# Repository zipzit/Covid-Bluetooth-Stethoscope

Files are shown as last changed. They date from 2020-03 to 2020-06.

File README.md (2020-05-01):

# Project description:  low-cost open-source DIY wireless stethoscope designs

(from [https://helpwithcovid.com/projects/252-bluetooth-stethoscope-pulse-oximeter](https://helpwithcovid.com/projects/252-bluetooth-stethoscope-pulse-oximeter))

This is a collaborative volunteer driven project to develop designs for low-cost wireless stethoscopes that can be constructed with hobbyist-level skill and tools and provided to medical professionals using the same volunteer-driven model current being used to create and donate face shield and masks world-wide.

## The problem

High-quality stethoscopes are expensive, and stethoscopes in general are hard to sterilize.  This results in a use model where cheap stethoscopes are acquired by the hospital/clinic and one is assigned to each patient, with every professional who works with that patient using the same stethoscope.  This can result in cross-contamination as someone touches many stethoscopes.  Cheap stethoscopes also wear out quickly and have short hoses, resulting in professionals getting physically closer to the patient than necessary, particularly if they have to put their arm around the patient and listen to positions on the back.

With Covid-19 this is an even greater problem because medical professionals may be wearing full PPE and struggle to get a traditional stethoscope into their ears safely.

Like N95 masks and face shields, there is concern that stethoscopes may become a scarce commodity as the pandemic continues to spread, and poorer countries with weaker healthcare systems will particularly struggle to source in-demand equipment.

## Our goal

To create stethoscope designs that reduce the risk of infection during use and cost of manufacture, and that can be built and validated by enthusiasts or manufacturers around the world, at price points that are viable in a variety of markets.

Current digital stethoscopes on the market start at $300-$500, and can go as high as $2700/unit. We are working towards the units being effectively disposable, to the point where if a hospital *had* to assign one to each patient and then throw it away when done it wouldn’t be a financial hardship.

In designing several different models we are targeting different price points and are able to deliver the simplest design fast.

## Our solutions

In order to reduce close physical contact between patient and medical professional we need an electronic device which can amplify or transmit the internal sounds created by the heart and lungs. Our lowest-tech concept design is a single hand-held device which picks up the sounds with a microphone and amplifies it to a speaker. More advanced designs will transmit that sound via Bluetooth to an over-the-ear headset worn by the medical professional. Our goal is to have the units be easily disinfected between uses so they can be utilized on multiple patients, but cheap enough that if necessary they could be assigned to a single patient as is the case with current stethoscopes.

This project is developing rapidly and constantly evolving. We are starting the simple amplifier + speaker and Bluetooth designs in parallel with the plan that learnings from one design can be applied to others. All designs are intended to be constructed by anyone with some basic electronics knowledge and a soldering iron, and possibly access to a 3D printer.

### "Quick-and-dirty" speaker puck

The simplest concept doesn’t use a headset at all - simply a single unit with a cup/microphone, a AA-battery-powered amplifier, and a speaker. We’re currently in the prototyping stage for this using off-the-shelf electronic components that anyone should be able to order online.  If possible, we would like to use existing containers - reusing standard pill bottles for instance - to avoid having to 3D-print a housing.

Sterilization is a factor as well.  If possible, using something like a pill bottle would provide a housing that can be easily sterilized.  If not possible, units can be placed in ziploc bags that can be sterilized between patients.  

#### Current status:
We still have some basic questions to answer to prove this solution can reliably reproduce and amplify lung sounds.  We have constructed a concept unit, but decent sound quality without creating feedback is proving to be a significant roadblock.  We are testing different directional microphones, mimicing stethoscope architecture, adding insulation between microphone and speaker, and exploring a setup with two units separated by a short cable. 

### "Smarter" speaker puck

One step up from there is to replace our simple analog electronics with some digital logic and a microprocessor.  We’re looking at the ESP32, which is common and relatively cheap, and there are a number of good development platforms on the market.  It comes with integrated bluetooth and wifi (which we would use for the next model), as well as lithium-ion battery charging logic.  This would allow us to potentially do some digital signal processing of the sound, to clear up noise or amplify certain frequencies.

This will build on the knowledge we gather about microphones and speakers and housings, and will likely require some software development.  It will take longer, so is the second stage solution.

#### Current status:
We have been working with two different ESP32 development boards - the ESP32-LoRa, and the ESP32 Lyra-T Mini:

Using the Lyra-T Mini we have constructed a prototype which uses a microphone inside a standard stethscope bell and broadcasts via bluetooth to a standard bluetooth-enabled speaker.  Heart sounds appear clear and audible though a Bose Soundlink bluetooth speaker, we need more work to determine if we can reproduce decent sound quality with an onboard speaker.  The Lyra-T Mini is approximately $22/unit and has extra on-board audio codecs and ADCs.

Using the LoRa, we have tested that we can pair reliably with most standard bluetooth devices, and recover the connection if one side of the link is reset.  We have modified the Espressif-provided open-source software to do this.  The LoRa has also had issues with the I2S DMA ADC operating while bluetooth is functional.  We filed a support ticket with Espressif and they have provided a fix.  The LoRa is slightly cheaper and smaller than the Lyra-T and comes with an onboard screen.  We would like this board as a development option, but it would require adding an addition codec/ADC chip - likely the ES8388, which is approx. $1. 

### Smart bluetooth puck

One step up from there is to enable bluetooth and the ability to pair with a set of over-the-ear headphones, worn by the medical professional over their PPE gear.  This will require some case redesign to allow for a small screen and some buttons, to allow selection of the bluetooth device to pair with.  Again, it builds off what we’ve learned from the previous design, and may require more software development.

To work towards a completed design we need to:
- Integrate the stethoscope cup or accept one attached by a short tube with a microphone.
- Develop whatever DSP (Digital Signal Processing) algorithms are necessary for noise/frequency filtering or shifting.
- Find an onboard amplifier/speaker solution that can reliably reproduce lung sounds with sufficient volume. 

#### Current status:
The "Smarter" Speaker Puck and Smart Bluetooth Puck are basically the same project at this point.  Our current prototype uses a standard stethoscope cup to pick up sounds, and a bluetooth link to connect to an external speaker.

To work towards a completed design we need to:
- Integrate the stethoscope cup or accept one attached by a short tube with a microphone.
- Integrate a screen that will show available bluetooth devices to pair with. (Requires software development)
- Test connections and audio quality with different bluetooth headsets (the cheaper the better).

### Unit testing collateral

Ultimately people who are constructing units will want standard metrics to test their units against.  We have audio recordings of lung sounds that we can devleop into an audio test library.  Another open-source medical devices organization (glia.org) has developed some promising-looking testing procedures using water balloons to mimic a human body.

For initial devices we will simply try to get devices in the hands of trained medical professionals for testing, but ultimately want to develop a standardized test plan.

### However...

Having said all of this, we are not inherently attached to these solutions.  We continue to look at alternate solutions (such as repurposing cheap earpods) to see if we can create better, cheaper, or more "quick-and-dirty" designs.

## What do we need?

We have a diverse, fast moving team of volunteers and are always looking for more support. If there is anything you are able to offer, please reach out to us, we are very welcoming of new team members.

Some skills we are particularly in need of:

* Electronics knowledge
* Software developers
* CAD engineers
* People who have 3D printers
* People to write documentation
* Fundraisers
* Project managers
* All-rounders!
* Manufacturers/distributors who think they could help

If you’re interested, please join through our [HelpWithCovid](https://helpwithcovid.com/projects/252-bluetooth-stethoscope-pulse-oximeter) page, and add us as a project you are interested in.  This will generate a message to us, and we can add you to the GitHub and you can join our Discord channel.

Thank you for reading this, and hope to see you soon!

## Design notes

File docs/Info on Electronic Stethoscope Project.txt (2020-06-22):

---Overview---------------------------------------------------------------------

    https://helpwithcovid.com/projects/252-bluetooth-stethoscope-pulse-oximeter

Scope:
    We're looking for a functional stethoscope that a doctor can use to listen
    to a patient's vitals, while wearing full protective gear.  A stethoscope on
    a hose is clumsy, not helpful with protective gear (facemask, hooded garment);
    additionally its ackward to disinfect a stethoscope between patients.  An ideal
    solution would be a device that could be wrapped in a disposable covering (perhaps
    a rubber glove?) between patients.

---Open Source Hardware Repos---------------------------------------------------

    https://en.wikipedia.org/wiki/List_of_open-source_hardware_projects

    https://en.wikipedia.org/wiki/List_of_open-source_health_software

    Screw it.. Github for the win.

---stupid dumb question for team - Stereo ?-------------------------------------

    LBC note: I was looking at the spec sheet for the AdaFruit MEMS microphone.
    You can use two for stereo.  Wow.  We each have two ears.  Is there any advantage
    to the quality of stethoscope use by providing true stereo performance?
    Perhaps an oval shaped cone? That would increase power usage, but it might
    be a big improvement in the quality of the device's output (?)

---Resources on hand------------------------------------------------------------

    LBC notes:

    3d printer makerbot, heated bed, working envelope:  225x145x150 millimeters or 8.9 x 5.7 x 5.9 inches
    material PLC (a small bit left) ABS (brand new unopened box)
    https://www.cnet.com/reviews/makerbot-replicator-review/
    https://picclick.com/MakerBot-Replicator-Dual-Extrusion-2-color-printing-3D-Printer-162737354718.html

    Hakko Fx-888 soldering iron.
    old skool power supply, old skool analog oscilloscope

    Access to Orange Pi's, Raspberry Pi's, ESP32 (with both Wifi and BT)

    At one point in time I started an inventory of my electronic parts.
    https://docs.google.com/spreadsheets/d/1TP7NCWNiXR75lc__cfYYinlH-1VoV7KbM1oV_g3vnZg/edit?usp=sharing
    I only have one microphone chip, a AdaFruit Mems development board (I2S)
    I'm going to check my buddies stock & steal (er, borrow) what he has available.
    He thinks he may have some electret condenser microphone elements available.
    I'm pretty sure he has a huge quantity of resistors and capacitors for most needs.

---Listening to heart rate---------------------------------------------------------

    https://forum.allaboutcircuits.com/threads/best-microphone-to-detect-heartbeat.155369/

    oops.  Heart rate isn't our primary objective.. its listening to a patient's
    lungs.

    Mike Vang's comment:
        Some of the boards out there like the MAX30100 can serve dual purpose such as
        getting SpO2 measurement and heart rate sensor.

        Including heart rate measurement is a feature that could always be adding if
        using something like a MAX30100 board.

---what about listening to lungs?-----------------------------------------------

    Nice overview paper.
    https://www.ncbi.nlm.nih.gov/pmc/articles/PMC6101681/
    Respiratory sound analysis in the era of evidence-based medicine and the
    world of medicine 2.0
    E Andrès,* R Gass,** A Charloux,*** C Brandt,**** and A Hentzler*****

    Kraman et al. [17] studied the effects of different microphones and concluded
    that the most effective one was the electret microphone with conical coupler,
    10-15mm in diameter;

    Frick, the Kraman study was done in 1995.  Way before cell phones high volume MEMS
    mikes... https://www.ncbi.nlm.nih.gov/pubmed/7555110/
    Measurement of respiratory acoustic signals. Effect of microphone air cavity
    width, shape, and venting.  Kraman SS1, Wodicka GR, Oh Y, Pasterkamp H.

    (oops. I only have mems microphone...)

    Electret vs mems?
    https://forum.digikey.com/t/electret-condenser-ecm-vs-mems-microphone/447
    Electret condenser microphone (ECM microphone) apply the principle of capacitor
    charge/discharge for operation. The diaphragm acts as one plate of a capacitor,
    the vibration is generated due to the sound, then produce the changes of
    charge between the plates to make the signal transmission.

    Since the vibration is purely an electromechanical mechanism, it has the
    whole acoustic frequency response (0-20kHZ) and low distortion in the signal
    transmission, generally used in external portable microphone. Its shortcoming
    is being unable to undertake a re-flow soldering, so there is a specific
    soldering process and tools for manual soldering.

---ESP-32-----------------------------------------------------------------------

    https://www.aliexpress.com/item/32801296418.html?src=google&src=google&albch=shopping&acnt=768-202-3196&isdl=y&aff_short_key=UneMJZVf&slnk=&plac=&mtctp=&albbt=Google_7_shopping&aff_platform=google&&albcp=9603941227&albag=96253190102&trgt=297309937605&crea=en32801296418&netw=g&device=c&albpg=297309937605&albpd=en32801296418&gclid=Cj0KCQjwpfHzBRCiARIsAHHzyZr4OGfWuGPSdq0CqLSSRd4H_1mqvi2yu0oduqNAtVLHI9zTAtB1Z9saAvgIEALw_wcB&gclsrc=aw.ds

    Power Consumption?
    https://esp32.com/viewtopic.php?t=2662
    VCC=5V     N. CORES ACTIVE: DEFAULT

    SCENARIO-------------------------------CPU80MHz-----------CPU160MHz---------CPU240MHz
    - CPU + ELECTRONICS + BT----------------113mA----------------123mA------------141mA
    - CPU + ELECTRONICS----------------------38mA---------------- 51mA ------------73mA
    - CPU (deep sleep) + ELECTRONICS--------3.5mA----------------3.5mA------------3.5mA

    AA battery (1.5v) life: 2400 mAhours
    AAA battery: 1000 mAhours

    Mike Vang's comment: https://www.tinycircuits.com sells lithium batteries.
        https://tinycircuits.com/collections/batteries
            All 3.7v; 70 mAH to 2500 mAH
           70 mAH   150 mAH     290 mAH     500 mAH     850 mAH     1000 mAH    1100 mAH    2500 maH
           $3.49    $3.95       $5.95       $6.95       $8.49       $9.95       $$9.95      $5.95

        Micro USB batter charger---$6.95

    While executing WiFi.scanNetworks() function very first time, module consumes
    average current of 0.5A for 10 ms with four peaks of approx. 0.7A during that
    period.  After that module consumes average 130 mA with 0.6A current spikes.
    The spikes have duration of 0.5 ms and appear in bursts with spike rate of 100 ms.

    Apparently it is about 2 times worse than promised in the ESP-32 data sheet.
    I expected to see about 0.3A max (50 mA for CPU and 240 mA max for WiFi
    transmitter).

    Can ESP32 handle I2S?  Can it perform A to D?
    https://demo-dijiudu.readthedocs.io/en/latest/api-reference/peripherals/i2s.html
    ESP32 contains two I2S peripherals. These peripherals can be configured to
    input and output sample data via the I2S driver.  The I2S peripheral supports
    DMA meaning it can stream sample data without requiring each sample to be
    read or written by the CPU.  I2S output can also be routed directly to the
    Digital/Analog Converter output channels (GPIO 25 & GPIO 26) to produce
    analog output directly, rather than via an external I2S codec.

    https://github.com/espressif/esp-idf  (Is this all ESP32's?)
    https://docs.espressif.com/projects/esp-idf/en/latest/esp32/hw-reference/index.html

---ESP32 General Specs----------------------------------------------------------

    https://en.wikipedia.org/wiki/ESP32
    Features of the ESP32 include the following:[3]

    Processors:
    CPU: Xtensa dual-core (or single-core) 32-bit LX6 microprocessor, operating
        at 160 or 240 MHz and performing at up to 600 DMIPS
    Ultra low power (ULP) co-processor
    Memory: 520 KiB SRAM
    Wireless connectivity:
    Wi-Fi: 802.11 b/g/n
    Bluetooth: v4.2 BR/EDR and BLE (shares the radio with Wi-Fi)
    Peripheral interfaces:
    12-bit SAR ADC up to 18 channels
    2 × 8-bit DACs
    10 × touch sensors (capacitive sensing GPIOs)
    4 × SPI
    2 × I²S interfaces
    2 × I²C interfaces
    3 × UART
    SD/SDIO/CE-ATA/MMC/eMMC host controller
    SDIO/SPI slave controller
    Ethernet MAC interface with dedicated DMA and IEEE 1588 Precision Time Protocol support
    CAN bus 2.0
    Infrared remote controller (TX/RX, up to 8 channels)
    Motor PWM
    LED PWM (up to 16 channels)
    Hall effect sensor
    Ultra low power analog pre-amplifier

---WebBlueTooth-----------------------------------------------------------------

    https://www.smashingmagazine.com/2019/02/introduction-to-webbluetooth/

    https://webbluetoothcg.github.io/web-bluetooth/
    Web Bluetooth -- Draft Community Group Report, 20 March 2020

    https://github.com/opengatt/registry

    Nordic Uart
    A generic service for reading and writing streams of bytes
    https://github.com/opengatt/registry/tree/master/services/uart
    Peripheral Implementations -- BLEStream Arduino
    Client Implementations -- ble-serial JavaScript (Node.js and Browser)

    Current status of audio over BLE (Android, iOS)
    https://www.silabs.com/community/wireless/bluetooth/forum.topic.html/current_status_ofau-u3gE

    LBC note: After looking closely at some of these details, I cannot imagine
    WebBlueTooth will manage a decent audio stream.  too much data.

    Never mind that this discussion was for the remote Telemedicine out of scope
    proposal.   A doctor needs to use a stethoscope to manage tube insertions to
    a patient right in from of them.  this is not a telemedicine conversation.

---Deals tied to the helpwithcovid.com site-------------------------------------

    See listing at: https://helpwithcovid.com/offers

    https://www.mygatorwatch.com/Default.asp
    Free watch (cell phone, geo locator) for elders in need. Interesting, but
    doesn't fit our proposal.  Might be a contact when it comes time for manufacturing...

    SMS texting from Chatbox...
    could be nice, not needed here. Ha.  Lost your stethoscope, send a text page.
    Er... no. just no...

    I was actually looking for server space.. and with current project scope that's
    unnecessary.

    Figma.com (great place to design a website...)  Design collaboration tool
    for teams to build software.  Not sure its a perfect match for a hardware team.

---Blood Oxygen level measurement?----------------------------------------------

    https://en.wikipedia.org/wiki/Pulse_oximetry

    Reflective Mode:

    These are good articles/papers about reflective-mode oximetry:
    https://www.sciencedirect.com/science/article/pii/S2405959516301205
    https://web.wpi.edu/Pubs/E-project/Available/E-project-042413-160152/unrestricted/Final_MQP_Report.pdf

    I don't see any currently available commercial reflective-mode solutions though.
    This article:  https://core.ac.uk/download/pdf/81961664.pdf  (page 2) shows a prototype reflective-mode circuit.  This has a
     microcontroller but otherwise doesn't look very complicated, we could possibly prototype one.

    Transmissive Mode:

    Apparently fingertip-or-earlobe oximetry is "transmissive mode" oximetry.  "Reflective mode" oximetry is possible at the
    wrists, chest or other sites, so this could theoretically be integrated into a stethoscope puck. The hardware is likely different
    than current market solutions, more research is necessary.

     If transmissive mode (fingertip) sensors would work, it's cheaper to source battery-operated units, one per patient.
     They look difficult to sterilize though.

    I found this Maxim Max30100 pulse oximiter/heartrate module and a review:
      https://www.teachmemicro.com/max30100-arduino-heart-rate-sensor/

    There are a couple different board versions, one is cheaper but harder to work with.
    The more expensive one is about $6/unit on Alibaba, don't know about availability.

    Mike Vang's comment:
        One could combine an electronic stethoscope with an oximeter.

        The paper that is shared below says that a reflectory pulse oximeter has more
        diverse locations it could take like from the feet, head, chest and wrist.
        Accuracy becomes an issue though.

        Reflectory pulse oximeter's has two LED's on one side (red and infrared). I
        think that many pulse oximeter like the Max30100 is a reflectory pulse
        oximeter.

        But we run into an issue: the base that touches the client is enlarged to
        include both a stethoscope and a pulse oximeter.

        Ref:
            https://www.sciencedirect.com/science/article/pii/S1877705812022060

---High Tech Question-----------------------------------------------------------

    Once you've gone digital, are there other tools we're interested in?
    e.g. Digital Signal Processing including filtering, Frequency domain analysis?

    LBC Note: I've recently finished the Coursera class (Mar 2018)--
    Audio Signal Processing For Music Applications
    https://www.coursera.org/learn/audio-signal-processing
    https://online.stanford.edu/courses/sohs-ymusic0001-audio-signal-processing-music-applications

    Meghana... the code work was all done in Python!

    At the time I wanted to use raspberry pi microphone for an interactive dynamic
    outdoor art project in downtown Las Vegas.  I also got bashed hard at a
    hackathon for a mining project, using a microphone / pi system to monitor
    pending mineshaft pump failures.  Great idea, i didn't really understand the
    nuances of Fast Fourier Transforms for live monitoring.  The class was
    really good at forcing you to understand what's going on.

---BlueTooth Linkup-------------------------------------------------------------

    The topic started as a conversation with my research scientist buddy Dirk,
    do we really need a visible screen?  And it gets down to how do you pair
    a digital stethoscope with a Bluetooth headset, if neither of them has a
    visible screen.  What if you are in a location that has lots of other
    Bluetooth devices present?

    One way is to lock the devices together using a dedicated "mac" address.
    You can permanently link the headset to a particular Bluetooth stethoscope.
    Easy to do when you are just making one set, not so easy to do when you need
    fifty or a 1000 of these.  And then if permanently paired, what happens
    when there is a problem with either (expensive) device?  You have to throw
    both pieces away.

    I think that means a OLED display screen is required, to manage the Bluetooth
    pairing process, sigh.  And momentary buttons for up / down / select.

    An exceptional reference on this stuff?  (ESP32, IOT stuff, Bluetooth)

    https://randomnerdtutorials.com/   From Rui and Sara Santos

    see:  Dedicated mac addresses for bluetooth devices.
          Blue tooth Advertising

---membrane?--------------------------------------------------------------------

    What to use for a stethoscope membrane?
    Ideas: sheet plastic
           plastic lid from a can of peanuts
           clean bottom of steel can
           Thin aluminum sheet (Coke Can)

---Open Source Licenses---------------------------------------------------------

    https://choosealicense.com/licenses/
    https://opensource.guide/legal/#which-open-source-license-is-appropriate-for-my-project

---Design of Experiments / Analysis of Variance---------------------------------

    ref: https://dogfeatherdesign.com/simple-design-of-experiments-analysis-of-variance-anova/

    Design Factors?
        --microphone type MEMS vs Electret Condenser microphone element
        --bell shape (parabola vs cone)?
        --Membrane material? (thin plastic sheet, thick plastic sheet, thin steel)
        --size of bell (big or small)
        --recording test master (what are we listening to?  Anybody have a
        master recording of the chest of someone with pneumonia? )

    Response (What's the measure of success?)
        idea: find a master recording of XYZ at a fixed volume level.
        (pick a couple of different ones)
        Play the master recording thru a speaker.
        Record with the digital stethoscope, perform FFT spectrogram analysis on
        the recording.

---Work of others in analysing Microphone performance---------------------------

    https://www.testandmeasurementtips.com/test-and-measurement-basics-of-microphones/

    google search terms: analyse different microphone performance using spectrogram

    https://en.wikipedia.org/wiki/Spectrogram
    A spectrogram is a visual representation of the spectrum of frequencies of a
    signal as it varies with time. When applied to an audio signal, spectrograms
    are sometimes called sonographs, voiceprints, or voicegrams. When the data
    is represented in a 3D plot they may be called waterfalls.

    https://link.springer.com/article/10.1007/s11334-019-00325-7
    Development and performance analysis of a low-cost MEMS microphone-based
    hearing aid with three different audio amplifiers
    Souvik Mallik, Debjyoti Chowdhury & Madhurima Chttopadhyay

    Interesting reference:
    https://superuser.com/questions/324469/spectrum-analyzer-that-shows-live-input-from-the-microphone

---Lung Sounds------------------------------------------------------------------

    https://www.youtube.com/watch?v=2NvBk61ngDY
    Lung sounds (respiratory auscultation sounds)
    Mar 7, 2018 -- Geeky Medics

    https://geekymedics.com/respiratory-examination-2/

---3D printed Stethoscope-------------------------------------------------------

    3D-Printed stethoscope:
    https://all3dp.com/3d-printed-stethoscope/

---Stethoscope with Core Attachment---------------------------------------------

    Attach-to-stethoscope page:  (removes all re-engineering of stethoscope)
    https://www.harriscomm.com/eko-stethoscope-with-core-attachment.html

---Stethoscope Design Information-----------------------------------------------

    How does a stethoscope work?
    https://www.scientificamerican.com/article/bring-science-home-stethoscope/ (kids basic info)

    https://www.ahajournals.org/doi/pdf/10.1161/01.CIR.34.5.899
    Stethoscope Acoustics
        II. Transmission and Filtration Patterns
        By PAuL Y. ERTEL, M.D., MERLE LAWRENCE, PH.D.,
        RICHARD K. BROWN, PH.D., AND AARON M. STERN, M.D.
        mention: Laennec wooden stethoscope of 1819. This is a straight rigid tube
        33.5 cm long with a bore diameter of 8 mm. It terminates in a shallow bell
        4.0 cm in diameter.

    https://www.maximintegrated.com/en/design/technical-documents/tutorials/4/4694.html
    INTRODUCTION TO DIGITAL STETHOSCOPES AND ELECTRICAL COMPONENT SELECTION CRITERIA
    By: John DiCristina
        A stethoscope must be most sensitive to cardiac sound in the 20Hz to 400Hz
        range and to pulmonary sound in the 100Hz to 1200Hz range. Note that the
        frequency ranges vary by manufacturer, and the DSP algorithms filter out
        sound beyond these optimal ranges.

    https://wiki.ece.cmu.edu/ddl/index.php/Stethoscope_opportunity
        (this looks like an engineering class project.  Lots of ideas there.)

    https://bmedesign.engr.wisc.edu/projects/file/?fid=2177
    UNIVERSITY OF WISCONSIN – MADISON: DEPARTMENT OF BIOMEDICAL ENGINEERING
    Electronic Stethoscope -- Fall 2011

    https://www.ncbi.nlm.nih.gov/pmc/articles/PMC4496820/
    https://www.ncbi.nlm.nih.gov/pmc/articles/PMC4496820/pdf/12938_2015_Article_56.pdf
    The electronic stethoscope
    Shuang Leng, Ru San Tan, Kevin Tshun Chuan Chai, Chao Wang, Dhanjoo Ghista,
    and Liang Zhongcorresponding author
        •• Thinklabs’ Rhythm 32 inventor, Clive Smith uses an electromagnetic diaphragm with
        a conductive inner surface to form a capacitive sensor. This diaphragm responds to
        sound waves identically to a conventional acoustic stethoscope, with changes in an
        electric field replacing changes in air pressure. This preserves the sound of an acoustic
        stethoscope with the benefits of amplification

    https://www.machinedesign.com/automation-iiot/article/21837541/the-stethoscope-gets-a-smart-iot-upgrade
    The Stethoscope Gets a “Smart” IoT Upgrade -- Engineers at John Hopkins University
    integrate AI, acoustics, and noise-canceling technology to modernize this
    humble medical device.
    Carlos Gonzalez     FEB 19, 2019
        The smart scope has an external microphone that records ambient sounds.
        The system uses active and adaptive acoustics to remove those sounds, in
        real time, from the digitized audio signal transmitted to the users ears.

    https://www.worthview.com/stethoscope-amplify-sound/
    Most of the times the rubes are made of rubber or any material that can create
    multiple reflections for the sound wave. When the sound wave vibrates the
    flat surface, it is directed to the rubber tube of the stethoscope. Then,
    the wave reflects inside the tube and travel to the ear tips. The direction
    is important to give accurate sound. The quality of rubber will determine
    the quality of sound the doctor gets through the ear tips.

    The high-pitch sounds directly vibrate to the flat disc of the diaphragm.
    However, the low-pitch sound uses the inside wave reflection through the bell.
    It picks the sound from the artery’s movement and moves outward to vibrate
    the bell. Then, it is directed to the tube and thus, the sound is amplified.

    https://en.wikipedia.org/wiki/Stethoscope
    oops. --> Rappaport and Sprague designed a new stethoscope in the 1940s, which
    became the standard by which other stethoscopes are measured, consisting of
    two sides, one of which is used for the respiratory system, the other for the
    cardiovascular system  (LBC note, which bell is for which?)

    And this -->  The simplest and least effective method of sound detection is
    achieved by placing a microphone in the chestpiece. This method suffers from
    ambient noise interference and has fallen out of favor. Another method, used
    in Welch-Allyn's Meditron stethoscope, comprises placement of a piezoelectric
    crystal at the head of a metal shaft, the bottom of the shaft making contact
    with a diaphragm. 3M also uses a piezo-electric crystal placed within foam
    behind a thick rubber-like diaphragm. The Thinklabs' Rhythm 32 uses an
    electromagnetic diaphragm with a conductive inner surface to form a capacitive
    sensor. This diaphragm responds to sound waves, with changes in an electric
    field replacing changes in air pressure. The Eko Core enables wireless
    transmission of heart sounds to a smartphone or tablet.

    https://insidefirstaid.com/diagnosis/the-best-littman-stethoscope-master-cardiology-and-classic-comparison
    Bells work similarly to diaphragms, but the hollow cavity in a bell has no
    membrane across it. Traditionally bells are used to listen to low frequency
    sounds.

    Although many stethoscopes come with a bell, there is disagreement in the
    medical community whether bells are useful or obsolete. Bells are traditionally
    thought to be better for hearing low-frequency sounds like some heart murmurs
    and bowel sounds while diaphragms are better for high frequency murmurs and
    lung sounds

    See also https://en.wikipedia.org/wiki/Pinard_horn

    https://uberdoco.com/blogs/news/stethoscope-bell-vs-diaphragm-a-comprehensive-comparison
    The bell is highly sensitive to low-frequency sounds. These are easily picked
    on the skin surface of the person being examined. The Diaphragm is sensitive
    to both low and high-frequency sounds. However, it is designed to filter out
    low-frequency sounds making it more sensitive to high-frequency sounds. The
    high-frequency sounds are amplified as the waves vibrate against the stiff
    membrane. This allows accuracy and clarity in the transmission of sound from
    the chest piece to the tubing and finally into your ears.

---Stemoscope-------------------------------------------------------------------

    https://www.stemoscope.com/
    Stemoscope - a commercially available Bluetooth listening device

    A quick run down: Stemoscope is not a medical device. It is marketed for STEM purposes.
    Features:
        Two listening modes:
            Bell mode (20-200 Hz) used for listening to heart beats
            Diaphram mode (100-500 Hz) used for listening to breathing
        Bluetooth
            Only works through phone app cannot be used with headphones/headsets
            Does not feature pairing
        App
            Supports:
                iPhones, iPads, iPad Touch w/iOS v7.0+ that supports BLE (Bluetooth Low Energy)
                Android 5.0+ devices that supports BLE
        Record samples into .WAV formats.
        Physical dimensions:
            38 mm in diameter and 11 mm thick
            ~1.5 inches in diameter and ~0.43 inches thick

    Stemoscope and it's role against COVID-19:
        https://www.stemoscope.com/stemoscope-in-fighting-covid-19-disease-lung-sounds/

    Stemoscope FAQ:
        https://www.stemoscope.com/faqs/

---Digital Recording Stethoscope------------------------------------------------

    https://multimedia.3m.com/mws/media/116424O/full-line-product-catalog-3m-littmann-stethoscopes.pdf
    This not exactly the same thing.  Its a stethoscope with a built in bluetooth
    enabled digital recorder, intended to allow a physician to send a recording
    to a nearby computer for further analysis.

    US$399 -- Littmann Electronic Stethoscope 3200
    US$299 -- Eko CORE Digital Stethoscope
    US$499 -- Thinklabs One Digital Stethoscope

    https://www.thinklabs.com/
    This is the stethoscope in the image with the wifi adapter and the apple earbuds.
    Thinklabs One solves auscultation via PPE. See Johns Hopkins preparation for COVID-19.

---Thinklabs and Covid 19-------------------------------------------------------

    https://www.thinklabs.com/covid19
    https://www.cbsnews.com/news/coronavirus-containment-dr-jon-lapook-60-minutes-2020-03-08/
    https://www.thinklabs.com/infectious-disease-and-biocontainment

    Biocontainment presents a unique challenge for auscultation. With the Centers
    for Disease Control calling for personal protective equipment (PPE) in treating
    patients for the coronavirus, how does the clinician place stethoscope eartips
    in the ears for listening? Auscultation at the bedside using a conventional
    style stethoscope with tubing becomes impossible.

    Thinklabs One's unique stethoscope design allows healthcare workers to perform
    ausculation while being protected in an isolation environment, and can be
    used with protective covers in the ED to reduce contamination when pre-screening
    admissions.

    The One can be used directly using earbuds or headphones, via bluetooth
    transmitters within the isolation room or to a consultant outside the room,
    connected to a loudspeaker, or send sounds via email or instant messaging on
    iPhone or iPad.

    PPE
    -Personnel are donning disposable earbud headphones inside PPE or headsets
     over PPE.
    -If inside, the earbud/headphone cable is then snaked out of the protective
     clothing, to be connected, external to the clothing, to the Thinklabs One
     Digital Stethoscope. The clinician can then listen clearly to patient sounds
     while being fully suited up.  (LBC notes...Ugh...  Really?  A bluetooth radio
     chip costs like $1.00 in production. Opinion: any manufacturer of anything
     with electrons, who doesn't include a bluetooth or wifi chip these days is
     dumb, if not just purely for marketing buzz and hype.)

    Ziploc Protection for Primary Care and ED
    -One group of researchers developed a simple and practical way to treat multiple
     infectious patients using resealable Ziploc plastic bags. They connected the
     stethoscope to a Bluetooth transmitter and then placed the device inside of
     up to ten-yes, ten-resealable Ziploc plastic bags. The bags were sequentially
     removed to reveal a clean surface for listening to patients.

    -The Ziploc method is a novel way to take advantage of the Thinklabs One form
     factor. The entire stethoscope and Bluetooth transmitter fit inside a sealed
     bag.

    -This is ideal for ED and primary care use, where protection is highly
     desirable, but PPE impractical.

    terms:
    ausculation - the action of listening to sounds from the heart, lungs, or
    other organs, typically with a stethoscope, as a part of medical diagnosis.
    ED - Emergency Department (?)

---ThinkLabs References---------------------------------------------------------

    Engineering Library and Downloads:
    https://www.thinklabs.com/user-manuals

    http://thinklabsone.com/AudacityManual/ThinklabsAudacityHelp.html
    A Free, Open Source, Cross-Platform Audio Editor -- Specially designed for
    Heart Sound and Lung Sound Visualization and Analysis

    https://www.thinklabs.com/sound-library
    The Sound Library is a collection recorded on Thinklabs stethoscopes
    by our user community.  Includes both heart and lung sounds.
    (oops.. nothing here)

    Instead check out the Thinklabs youtube channel,
    https://www.youtube.com/playlist?list=PLLKSXV1ibO86qgE2y9cMqNFmh6LfOa8RM
    Lung Sounds -- 15 videos

---GrabCad Stuff----------------------------------------------------------------

    Lots of reference stuff available at https://grabcad.com/library
    including a whole bunch of Covid PPE devices and related work of others.

    https://grabcad.com/library/digital-stethoscope-1
    digital stethoscope
    Adriano Ordoz Barissa (Cravinhos, Brazil)
    October 11th, 2017
    The idea for this product is to make a stethoscope easy to use in order to be
    used in hospitals and residences.  (LBC note.  I sent a note to Adriano thru
    grabcad, asking for input, perhaps get him to join team. 3/29/2020, 4:30PM PST)

---Idea-------------------------------------------------------------------------

    ESP32 devices have multiple wireless Inputs/output systems.  We could use
    bluetooth for heart/lungs audio, and use an other channel for battery life
    monitoring (I'm thinking a hospital has 20 of these things.. How many have low
    batteries?)  LoRa band can easily handle that little bit of IoT (internet of things)
    traffic, reminding hospital folks that units 1, 9 and 13 are running low and need
    to be charged...

---ESP32 Testing----------------------------------------------------------------

    https://www.espressif.com/sites/default/files/documentation/esp32_datasheet_en.pdf

    https://randomnerdtutorials.com/getting-started-with-esp32/
    https://randomnerdtutorials.com/installing-the-esp32-board-in-arduino-ide-windows-instructions/
        Example, scan wifi hosts.  Works well.
    https://create.arduino.cc/projecthub/zipzit/esp32-hello-world-blinky-0c4a16

    Heltec htit-w832
    https://robotzero.one/heltec-wifi-kit-8/
    Use Board "Heltec WiFi Kit 32"
    Examples -- WiFi -- WiFi Scan

    Oled display library: https://github.com/olikraus/u8g2
    File> Examples > U8g2 > full_buffer > GraphicsTest
    Doesn't seem compatible with Heltec chip.

    https://www.youtube.com/watch?v=dk-01OpKYuQ
    Using Heltec ESP32 OLED Wifi Kit
    Sep 11, 2019 -- Robojax
        Support:
        https://robojax.com/learn/arduino/?vid=robojax_ESP32_Heltck_OLED
        https://github.com/HelTecAutomation/Heltec_ESP32

    Arduino IDE, File --> Preferences --> Add https://docs.heltec.cn/download/package_heltec_esp32_index.json
    tp Additional Board Manager URLs (via button on the right)

    then board --> Board manager --> heltec   and install...
    oops, https://docs.heltec.cn/download/package_heltec_esp32_index.json = file not found...
    use http://resource.heltec.cn/download/package_heltec_esp32_index.json

    https://heltec.org/project/wifi-kit-32/
    https://heltec-automation-docs.readthedocs.io/en/latest/esp32/quick_start.html

    tools --> Board --> Boards Manager, search for Heltec ESP32... install..

    After installation Tools --> Board --> Select Heltec ESP32 Arduino  --> WiFi Kit 32

    Open Arduino IDE, then Select Sketch->Include Library->Manage Libraries... Search Heltec ESP32 and install it.

    great.  Everthing works in the example file.

---Oled Graphics Display--------------------------------------------------------

    How do they create the oled logos?
    const unsigned char LoRa_Logo_bits[] PROGMEM = { 0x00, 0x00, ...
    https://arduino-esp8266.readthedocs.io/en/latest/PROGMEM.html
    https://esp32.com/viewtopic.php?f=13&t=4780

    ref:  https://lastminuteengineers.com/oled-display-arduino-tutorial/

    How do you design things this way?

    https://www.youtube.com/watch?v=Q1iVtLQOZOI
    How to convert images to Arduino Arrays for use on LCD displays! - Tutorial
    Mar 19, 2018    Brainy-Bits
        https://sourceforge.net/projects/lcd-image-converter/
        This program allows you to create bitmaps and fonts, and transform them
        to "C" source format for embedded applications.  The transformation of
        the images to the source code is made by using templates. Therefore, by
        modifying the templates, you can change the format of the output within
        certain limits.

    https://learn.sparkfun.com/tutorials/flexible-grayscale-oled-hookup-guide/all
        https://github.com/sparkfun/BMPtoArray  (python script)
        This script takes in a bitmap and converts the bitmap into 4-bit grayscale.
        An array of bytes is generated that can be copy/pasted into a header file.

    https://www.spriters-resource.com/

---Digital Signal Processing on a DSP32. Possible?------------------------------

    I was thinking about the simple in/out audio box design.  What if we needed DSP
    filtering?  Not sure ESP32 is the best choice, but its available and
    relatively inexpensive.

    Wow.  I'm surprised that this library exists.
    https://github.com/espressif/esp-dsp
    https://hackaday.io/project/166122-esp32-as-bt-receiver-with-dsp-capabilities

---Microphone to Speaker design 101---------------------------------------------

    https://circuitdigest.com/electronic-circuits/simple-microphone-to-speaker-circuit
    Simple Microphone to Speaker Amplifier Circuit    BySourav Gupta Nov 13, 2018
        Electret Mic, Opamp, Speaker.. oops. this one is 12v, I'd like to stay in 3.7v
        to 6 volt range.  Also no volume control. Did we say this was simple?

    Google searching for this stuff we see designs all the way from BJT transistor
    trains thru OpAmp designs to inexpensive integrated circuit chips with
    everything already built in.  Charley's guidance is clear. Don't reinvent the
    wheel.  Existing IC's it is!

    Interesting reference:
    http://www.electronoobs.com/eng_circuitos_tut13_1.php
    check out the boost converter to the amp circuit (3.7v --> 12vdc)

---Amplifier Chips--------------------------------------------------------------

    There are two ways to go here for a Maker type solution (soldering, no smc soldering).
    1) Opamp with dip pins in prototype drilled board with discrete components
    2) AdaFruit type solution with integrated Audio Amp SMC boards on breakout board.

    Amplifier chips?
    http://www.ti.com/audio-ic/amplifiers/speaker-amplifiers/products.html?pqs=paqs&familyid=3419#p2982=Analog%20Input&p1055max=Mono&p2622min=2;2.5&p2622max=3;6&p342=0.047;5

    Dumb system?  Control Interface = hardware, not gpio.  What about pseudo discrete
    gain amounts.  See the jumper on the AdaFruit board.  You would set a jumper once
    then simple on-off.  Easy Peasy.  Will that work?

    https://www.adafruit.com/product/987     $8.95
    Stereo Amp, Class D.   2 x 3.7W channels into 3 ohm impedance speakers.
    uses jumper to control gain 6dB default, set 9-18 with jumper. Inputs routed
    thru 1.0uF capacitor. Output Power: 3.7W at 3Ω, 10% THD, 1.7W at 8Ω, 10% THD,
    with 5V Supply  uses MAX98306  Digikey # 1528-1380-ND

    Are there other Audio Amplifier Evaluation Boards that will work for us?
    https://www.digikey.com/products/en/development-boards-kits-programmers/evaluation-boards-audio-amplifiers/789
    Filter: in stock.  Sort by price, have a nice day.

    1528-1492-ND  Adafruit Industries LLC	2.5W CLASS D AUDIO AMPLIFIER  $3.95   Mono IC: PAM8302A
    1528-1696-ND  Adafruit Industries LLC	MAX98357A I2S AMP BREAKOUT BOARD 3.2W $5.95  Mono IC: MAX98357A
        (oops, I2S audio input only, good for I2S Mems microphone, not for Electret)
    1738-1068-ND  DFRobot	3W MINI AUDIO STEREO AMPLIFIER  $5.96  Stereo  IC: PAM8403
        (DO NOT apply over 5.5V, it damage the chip presently)
    1568-1025-ND  SparkFun Electronics	TPA2005D1 AUDIO AMP MONO 1.4W  $7.95  Mono  IC: TPA2005D1
    1528-1380-ND  Adafruit Industries LLC	AMP AUDIO 3.7W CLASS D  $8.95 Stereo IC: MAX98306
        https://datasheets.maximintegrated.com/en/ds/MAX98306.pdf
        Lots of features here, including jumper settings for different gains.
        Five pin-selectable gains: 6dB, 9dB, 12dB, 15dB and 18dB. Designed for
        3 ohm speakers (is that an issue?)
    1528-1193-ND	Adafruit Industries LLC	BREAKOUT STER 2.8W AMP D TS2012	73	$9.95
        Class D	2-Channel (Stereo)	2.8W x 2 @ 4Ohm	2.5V ~ 5.5V	TS2012	Onboard
        dip switches for gain settings, comes with input capacitor
    1528-1381-ND	Adafruit Industries LLC	AMP AUDIO 2.8W CLASS D	49	$9.95
        Class D	2-Channel (Stereo)	2.8W x 2 @ 4Ohm	2.5V ~ 5.5V	TPA2016D2
        "I2C control input for gain.  nice for ESP32. Settings are not stored in
        the chip, so you'll need to adjust any gain & AGC amplification settings
        every time the amp is powered up."
    1738-1055-ND  DFRobot	386AMP AUDIO AMPLIFIER MODULE 500mW  $14.19 Mono IC: LM386
        ( too small wattage, but the chip is interesting )

    ref notes:
    https://www.instructables.com/community/What-IC-should-I-use-to-make-a-microphone-to-speak/

---Volume adjustment, Analog Design---------------------------------------------

    Oops. Missed this first time thru.  In the AdaFruit data sheet for the
    audio amp, there is a note on pg. 8 of 15
    "For volume control, a dual 50K audio taper pot can be wired in series
    with the inputs as shown"

    ref: AdaFruit audio amp 3w dev board uses MAX98306 chip.pdf

    Obviously with a mono speaker in/out we don't really need the dual pots.
    Search criteria at Digikey:  in Stock, Logarithmetic, value 50K, sort by price.
    But wait.. I do see some pots that include an on/off switch built in.  Either
    push on/off or rotate to power off. That would help us greatly.  Need a bit more
    research here.  In the meantime I have access to linear 50K pots that will work
    in testing until phase 2 delivery of parts from Digikey...

    What about a dual on off switch and potentiometer?  That would be nice to have.
    https://www.digikey.com/products/en/potentiometers-variable-resistors/rotary-potentiometers-rheostats/84
    search criteria: In Stock, Resistance 35K to 75K,
    Switch:  Push Push, Rotary, Detent (Avoid Push Pull, avoid Momentary)

    Something is definitely amiss here.  All the digikey logarithmetic variable
    pots that include on/off switches are 10K ohms. All the old school audio
    amplification circults using opamps reference 10K ohm log pots. Not sure why
    Lady Ada recommended the 50K pots. It would SURE BE HANDY on the low end
    system to have an integrated on/off/volume single knob.  I know we talked about
    always on and that is certainly an option.  We really need to test this stuff.

    My tendency is to purchase some switch 10K pots, a 25K pot, a 50K pot and a 100K pot and
    see what makes sense after we power up the original prototype.  Its not at all
    clear on how this will sound. Lets try it and see.  Extra parts go back into
    the bin for next project.

    What we really want is Bourns PTR902-2020K-A503-ND
    https://www.digikey.com/number/en/bourns-inc/118/PTR902/121459?k=&pkeyword=&sv=0&pv1=238015&sf=0&quantity=&ColumnSort=0&page=1&pageSize=25&bpn=118-121459
    PTR902-2020F-A503
    Non stocked item, 180 quantity of order, 16 Weeks, have a nice day.  ‎

    Some discussion items on resistor selection:
    https://electronics.stackexchange.com/questions/101259/audio-from-arduino-dues-analog-outputs-using-lm386

---Base Boost from OpAmp?-------------------------------------------------------

    http://www.ti.com/lit/ds/symlink/lm386.pdf
    See para. 9.2.5, LM386 with Bass Boost
    how does that work?

---System Requirements - Thoughts-----------------------------------------------

    3 to 5 watts?
    Juice: 2 to 6v
    Speaker: 4Ω

    Architecture: Class-AB, Class-D
    https://www.powersoft-audio.com/en/support/faq-s/113-rack-amps-faqs/1122-what-is-the-difference-between-class-ab-and-class-d-technology

    Closed/Open Loop:  (huh?)
    Open Loop -- The output assumes one of the two possible states, that is +V(sat)
         or -V(sat) and the amplifier acts as a switch only. This is used in
         rare applications like voltage comparator, zero crossing detector, etc..
         The op-amp works as a high gain amplifier.
    Closed Loop -- The utility of an op-amp can be greatly increased by providing
        negative feedback.  The output in this case is not driven into saturation
        and the circuit behaves in a linear manner.

    (ref: https://www.slideshare.net/GOWRISHANKARRAJU1/slew-rate-open-and-closed-loop-configurations)

---US based electronics suppliers-----------------------------------------------

    Mouser
    Digikey
    Newark Electronics
    Arrow Electronics

---Microphone references--------------------------------------------------------

    https://www.adafruit.com/product/1063
    ELECTRET MICROPHONE AMPLIFIER - MAX4466 WITH ADJUSTABLE GAIN
    20-20KHz electret microphone
    This is a convenient package with some interesting features. Worth understanding,
    On the back, we include a small trimmer pot to adjust the gain. You can set
    the gain from 25x to 125x. That's down to be about 200mVpp (for normal speaking
    volume about 6" away) which is good for attaching to something that expects
    'line level' input without clipping, or up to about 1Vpp, ideal for reading
    from a microcontroller ADC. The output is rail-to-rail so if the sounds gets
    loud, the output can go up to 5Vpp!

    Using it is simple: connect GND to ground, VCC to 2.4-5VDC. For the best
    performance, use the "quietest" supply available (on an Arduino, this would
    be the 3.3V supply). The audio waveform will come out of the OUT pin. The
    output will have a DC bias of VCC/2 so when its perfectly quiet, the voltage
    will be a steady VCC/2 volts (it is DC coupled). If the audio equipment you're
    using requires AC coupled audio, place a 100uF capacitor between the output
    pin and the input of your device. If you're connecting to an audio amplifier
    that has differential inputs or includes decoupling capacitors, the 100uF cap
    is not required.  The output pin is not designed to drive speakers or anything
    but the smallest in-ear headphones - you'll need an audio amplifier (such as
    our 3.7W stereo amp) if you want to connect the amp directly to speakers.
    If you're connecting to a microcontroller pin, you don't need an amplifier
    or decoupling capacitor - connect the OUT pin directly to the microcontroller
    ADC pin.

    AdaFruit MAX98357A I²S 3W Class D Amplifier Breakout Board

---Microphone Selection---------------------------------------------------------

    Digikey: https://www.digikey.com/products/en/development-boards-kits-programmers/evaluation-and-demonstration-boards-and-kits/787
    I started here for the quick and dirty easy to solder and test microphone boards
    with components already attached.  My initial thought was to obtain one mems
    microphone and one Electret (nearest the medical white paper dimensions)
    and move this along.  I was surprised what I found in the dev board stuff here.

    Digi-Key Part Number	Manufacturer	Description	Quantity Available	 Unit Price (USD) 	Function	Utilized IC / Part	Primary Attributes
    1528-2521-ND	Adafruit Industries LLC	PDM MEMS MICROPHONE BREAKOUT	224	 $4.95 	MEMS Omnidirectional Microphones	MP34DT01-M	-
    1528-1362-ND	Adafruit Industries LLC	BREAKOUT BD SIL MEMS MIC SPW2430	127	 $4.95 	MEMS Omnidirectional Microphones	SPW2430	Analog Output
    1528-4346-ND	Adafruit Industries LLC	PDM MICROPHONE BREAKOUT WITH JST	149	 $4.95 	MEMS Omnidirectional Microphones	MP34DT01-M	-
    1528-1908-ND	Adafruit Industries LLC	SPH0645LM4H I2S MICROPHONE BOARD	84	 $6.95 	MEMS Omnidirectional Microphones	SPH0645LM4H	-
    1568-1037-ND	SparkFun Electronics	ADMP401 MEMS MICROPHONE	0	 $10.95 	MEMS Omnidirectional Microphones	INMP401	-
    102-6243-ND	CUI Devices	MEMS MICROPHONE EVAL BOARD	305	 $12.64 	MEMS Omnidirectional Microphones	CMM-2718AB-38308-TR, CMM-2718AT-42308-TR, CMM-4030DB-26354-TR, CMM-4030DT-26354-TR	-
    102-6242-ND	CUI Devices	ECM MICROPHONE EVAL BOARD	105	 $15.30 	Electret Condenser Microphones	CMC-4013-SMT-TR, CMC-6015-47P, CMM-3312AT-44308-TR, CMR-2747PB-A	-

    That last Electret board in interesting.  Its intended to be split into four
    parts, three different electret mics and one mems mic.  Might be a good way
    to test.  3 electret mics are: omnidirectional, noise cancelling and
    unidirectional.  The mems mic is omnidirectional.

    If I had to guess, I'd suspect we want unidirectional microphone.  Don't
    really know. It would be fun to test each to understand how each works.

    Microphone search: https://www.digikey.com/products/en/audio-products/microphones/158
    filters:  On hand, shape = round, type = Electret Condenser & magnetic,
              Size/Dimension = 9.4 and 9.7mm, (Direction = Unidirectional)

---CUI Inc Microphone dev board supplier----------------------------------------

    https://www.cuidevices.com/
    CUI Devices
    6405 SW Rosewood St, Ste C
    Lake Oswego, OR 97035
    1-877-323-3576
    Phone: 971-335-3648

    Odd. I was looking for info on microphones, but their website only shows power
    related products.  Not sure what that means.  We'll have to call during
    the daytime and ask.  I really hate spec'ing out a product that is no longer
    in production, or is not supported.

    oops.  check out https://www.cuidevices.com/   Its a different website.

    mic5 = CMM3312AT-44308-TR (MEMS, Omnidirectional)
    mic6 = CMR-2747PB-A (Electret, Noise Cancelling)
    mic7 = CMC-6015-47P (Electret, Unidirectional)
    mic8 = CMC-4013-SMT-TR (Electret, Omnidirectional)

    On Thursday, April 2, 2020, 03:20:59 PM PDT, CUI Devices - Tech Support
    <techsupport@cuidevices.com> wrote:
        LB, each of the 4 pieces is a 0.59” x 0.59” square and the board thickness
        is 0.032”.  Let me know if you need anything else.

        Best Regards,
        Ryan Smoot
        Applications Engineer
        CUI Devices
        Direct: 971.335.3613
        Toll Free: 877.323.3576
        www.cuidevices.com

---Speakers?--------------------------------------------------------------------

    (initial sorted via price... that may not have been the best way... See notes below on Freq Self Resonant)
    Soberton 433-1220-ND 4Ω, 0 to 8khz, 92db, $2.46, Rated power: 1.5W, Max power: 300mW 28mm dia, 4.4mm height
    Soberton 433-1182-ND 4Ω, 102dB efficiency,  $3.32, Rated power: 3W, max power: 4W round speaker, rect frame, 77.2x77.2x21mm
    Soberton 433-1175-ND 4Ω 0hz to 7kHz, $3.39 rated power: 1W, max 2W, 26.3mm OD x 12.5
    Soberton 433-1173-ND 2Ω (yup, 2Ω) 0Hz to 20kHz, $3.52 rated power: 1W, max 2W, 26.3mm OD x 12.5
    Soberton 433-1246-ND 4Ω 0Hz to 10kHz, $3.63, rated power 1W, max: 1.5, 27x20x6.4mm (laptop speaker?)
    PUI Audio 668-1420-ND, 4Ω 100Hz to 20kHz, $4.23, rated power 2W, max 5W, 70x30.5x24mm rectangular shape.
    Soberton 433-SP-3616-ND, 4 OHM, 2.5W, 80DB, 190HZ,36MM DI, $5.46, Rated power 2W, Max 3W, 36mm dia x 16.3mm
    Soberton 433-1176-ND, EXCITER 3W, 4 OHM, 0 to 8kHz, $5.48, Rated power 3W, max 4W,  33MM dia X 12.3MM
    Soberton 433-SPM-3040L-ND, 4 OHM, $5.73, 0 to 10kH, Rated power 2W, max 3W,  2.5W, 86DB, 40x30x15 plastic enclosure.
         (unusual simple plastic enclosure. this might work well with battery reloading and simple housing design)
    PUI Audio, Inc.	668-1359-ND, SPEAKER 4OHM 3W TOP PORT 86DB, rare earth mgnt. 100Hz-20kHz, rated power 3W, max 4W, 40mm dia x 17.5mm

    I'm thinking the round speakers are probably easier to package.
    search terms: shape: (Round, Round with Rect frame, Round with Sq Frame),
    Power Max (3 to 6 W), Stock = on Hand.
    Sort by Self Resonant Frequency, smaller is better for us.  See note below.

    https://www.digikey.com/products/en/audio-products/speakers/156?

    There are a whole lot of speakers that seem to work;  Its not clear on what some
    of these characteristics are:  e.g Frequency Self Resonant (?),
    does moisture protecting rating matter to us?  Would exciters offer us anything?
    (hm.. can we use an exciter as an input device?  I know I've taken cheap speakers and
    used them as microphones and they work. Do exciter speakers offer us anyting?
    Might be worth a call to the engineers at PUI Audio and find out. See also
    Surface Transducer note, below )

    I copied info to online spreadsheet, sorted by Frequency Self Resonant.  My #1 choice is
    668-1359-ND	AS04004PR-R	PUI Audio, Inc.	SPEAKER 4OHM 3W TOP PORT 86DB	3122	$6.71
        FSR= 180Hz  Size: 40mm dia x 17.5mm

    Backup Speaker Selection:
    2104-SP520104-1-ND	SP520104-1	DB Unlimited	DYNAMIC SPEAKER	1888	$8.39
        FSR = 150Hz  Size: 52mm dia x 28mm
        why?  Different manufacturer, larger size, lower FSR rating.

---PUI Audio - Speaker Mftr-----------------------------------------------------

    puiaudio.com
    PUI Audio
    3541 Stop Eight Rd.
    Dayton, OH 45414
    P937.415.5901
    Eaudio@puiaudio.com

    Sound library: http://www.puiaudio.com/resources-sounds.aspx
    white papers: http://www.puiaudio.com/resources-white-papers.aspx

---Speaker Self Resonant Frequency----------------------------------------------

    https://www.stetron.com/resonant-frequency/
    In the piston range of a driver (before the cone exhibits oscillations other
    than those induced by the motion of the voice coil in the magnet), a loudspeaker
    acts as a high pass filter (HPF). The resonant frequency of a speaker, f0
    (pronounced: F-naught), is the frequency below which a loudspeaker is
    increasingly unable to generate sound output for a given input signal.

    https://www.proaudioland.com/news/the-importance-of-a-speakers-resonant-frequency/

    LBC Note:  oops.  I think that means we need to find speaker that are on
    the low end of Self Resonant Frequency, when we prioritize them for low
    frequency output.  Wish i'd seen that before, sigh.

---White Paper on Stethoscope---------------------------------------------------

    Discord note from bamboo, 4/3/2020 at 9:20 PM
    Not sure if folks have seen this paper.
    https://www.ncbi.nlm.nih.gov/pmc/articles/PMC5757962/
        2018 Jan 4
        Digital stethoscope: technology update
        Supreeya Swarup and Amgad N Makaryus

    Charley Lucas - Woodinville WA 4/4/2020 at 12:25 AM
    That paper led me to this 24-page analysis of electronic stethoscopes...  it's
    mostly telehealth related, but they've done some consistent measurements
    across a whole range of different stethoscopes (one costs $2700!), so if we
    try to follow their model we can compare with those.

    http://telehealthtechnology.org/toolkit/electronic-stethoscopes/
        TTAC
        Electronic Stethoscopes

    bamboo, 4/4/2020 at 1:21 AM
    I thought this one was also good.  Just more background info.
    https://www.ippt.pan.pl/Repository/o5918.pdf
        "Sound differences between electronic and acoustic stethoscopes"

    https://www.ahajournals.org/doi/pdf/10.1161/01.CIR.34.5.889
    Stethoscope Acoustics
        I. The Doctor and His Stethoscope
        By PAUL Y. ERTEL, M.D., MERLE LAWRENCE, PH.D.,
        RICHARD K. BROWN, PH.D., AND AARON M. STERN, M.D.

    -- This paper is generally focused on measuring performance.
    -- "Controversy has long existed as to whether the mechanical stethoscope is
       capable of amplifying sound. Data from both the objective and the subjective
       studies indicate that it can amplify. However, amplification was found to
       be uneven in all instruments in which it did occur. The regularity of
       amplification peaks occuring through the test frequency range suggests that
       these peaks reflect standing waves within the lumen of the stethoscope.
       These occur when the length of a stethoscope matches quarter-wave lengths
       of the sounds passing through it. This results in reinforcement, commonly
       called "resonance peaks." Other factors may be involved, and specific
       studies must be carried out with instruments of constant length before
       this concept can be validated."

    https://www.sciencedirect.com/science/article/abs/pii/0002870351901561?via%3Dihub
    The effects of tubing bore on stethoscope efficiency
    Maurice B.Rappaport, E.E.    Howard B.Sprague, M.D.
    -- Our data showed that below about 100 cycles per second, the efficiency is
       not affected materially by tubing length. From about 100 cycles per second
       to 1,000 cycles per second, tubing length exhibits a considerable effect
       upon stethoscope efficiency; that is, the efficiency decreases with increased
       tubing length. We concluded that the changes in the efficiency of an acoustic
       stethoscope which are caused by varying the length of the tubing, although
       not given any consideration by stethoscope users, produce an effect upon
       the quality of the heart sounds and the ability to hear low-intensity murmurs of
       medium and high frequency. For example, at 200 cycles per second there is a 15
       decibel attenuation of the sounds when two rubber tubes, each 26 inches long
       (commercial stethoscope tubing, with a caliber of 3/16 inch), are substituted for
       two similar tubes 3 inches in length. The sound is about eight times as loud in
       the short tubing system. This attenuation occurs in the region where the lowintensity,
       high-pitched basal diastolic murmurs are present, and every possible
       increase in efficiency in this region is of utmost value.
       Our analysis also indicated that the auscultatory sound
    -- Our analysis also indicated that the auscultatory sound pressure variations
       at the ear, produced by the motion of the skin or Bakelite diaphragm, are inversely
       proportional to the internal volume of the stethoscope, so that an infinitely
       small volume would theoretically exhibit a maximum variation in pressure,
       which, in turn, would manifest itself as a sound of maximum intensity. The
       skin diaphragm effect is produced when the open bell chest piece is placed on the
       surface of the chest, and the Bakelite diaphragm effect is produced by means of
       the Bowles chest piece. Obviously, therefore, the tubing, according to this form
       of reasoning, should be as short as possible and the caliber as small as possible.
       Also, the wall of the tubing should be sufficiently rigid for maximum efficiency,
       for any wall motion reduces the effective pressure variation transmitted to the
       observer’s ear.
    -- We also indicated that a factor that must be taken into consideration is the
       frictional resistance offered to the air column by the walls of the rubber tubing.
       That is, the efficiency of a stethoscope decreases as the resistance to the pressure
       variations is increased; the resistance is increased as the caliber is decreased.
       In eliminating the resistance component, we have still to consider that the greater
       the volume, the less the efficiency.

    https://www.ncbi.nlm.nih.gov/pmc/articles/PMC6076413/pdf/12938_2018_Article_540.pdf
    https://biomedical-engineering-online.biomedcentral.com/track/pdf/10.1186/s12938-018-0540-2
    Sound diferences between electronic and acoustic stethoscopes
        Lukasz J. Nowak and Karolina M. Nowak

    https://jidc.org/index.php/journal/article/view/24423717/985
    Stethoscope disinfection campaign in a Nigerian teaching hospital: results of a before-and-after study
    Chigozie J. Uneke

    https://biomedical-engineering-online.biomedcentral.com/track/pdf/10.1186/s12938-015-0056-y
    The electronic stethoscope
        Shuang Leng, Ru San Tan, Kevin Tshun Chuan Chai, Chao Wang, Dhanjoo Ghista and Liang Zhong

    https://www.ncbi.nlm.nih.gov/pmc/articles/PMC4864738/pdf/mbp-21-178.pdf
    Comparison of stethoscope bell and diaphragm, and of stethoscope tube length,
    for clinical blood pressure measurement
        Chengyu Liua,c, Clive Griffithsa, Alan Murraya and Dingchang Zhenga

    https://www.ncbi.nlm.nih.gov/pmc/articles/PMC1017790/pdf/brheartj00363-0111.pdf
    A NEW DIAPHRAGMATIC STETHOSCOPE
        C. R. Burch and J. P. P. Stock (1961)

    https://academic.oup.com/eurheartj/article/37/47/3536/2844988
    The 200th anniversary of the stethoscope: Can this low-tech device survive
    in the high-tech 21st century?
    Ivan Bank1,2, Hubert W. Vliegen3, and Albert V.G. Bruschke

    https://www.ncbi.nlm.nih.gov/pmc/articles/PMC5783442/pdf/abc-109-06-0606.pdf
    Lung Ultrasound: The Cardiologists' New Friend
        Marcelo Haertel Miglioranza, Antonio Carlos Sobral Sousa, Caroline de Souza Costa Araujo,
        Marcos Antonio Almeida-Santos,  Luna Gargani

---Outside of the box thinking, Surface Transducer------------------------------

    Digikey 1568-1619-ND  SparkFun Electronics $24.95 (oops, only one left)

    Surface transducers give you the awesome power to turn almost any surface into a
    speaker. They’re essentially just a speaker except instead of a cone, the coil is attached to a pad
    that conducts the vibration into whatever you press it against. Hook it up to an audio source and
    press it against the nearest table, wall or cardboard box. You can even put it against your head and
    play music directly into your skull (the ultimate surround sound).
    Dimensions: 50mm in diameter, 31mm tall

---Premade containers?----------------------------------------------------------

    Opportunities here include:
        Reduced requirement for a 3D printer.
        Ease of disinfect process
        Ease of changing batteries
    Risks?
        Will this work for sound pickup / transmission ?
        Need to find inexpensive, readily available containers.

    Medical / Pill Jars?
    Rubbermaid Blister Pack Containers?
    Small metal paint cans?
        https://www.amazon.com/Cornucopia-Metal-6-Pack-Unlined-Quarter/dp/B082DM7FZX/ref=sr_1_2
        SIZE: 2.25 inch tall x 2.5 inch diameter
    Other containers?
        https://catalog.uline.com/Spring-Summer-US-2020/585/
        https://www.uline.com/Product/Detail/S-9934/Jars/Clear-Round-Wide-Mouth-Plastic-Jars-4-oz-White-Cap
        4 oz container, 2" id, 2.72" tall, $0.46 each (clear), $.40 ea opaque, 36 to a case.
            https://www.uline.com/PDF/RS-14506-SPFR.pdf
        3 oz container, 2" dia, 2.13" overall height,
            https://www.uline.com/PDF/RS-17034-SPFR.pdf
        2 oz container, 1.875" dia x 1.87" height.  $0.39ea , 48 to a case
            https://www.uline.com/PDF/RS-12752-SPFR.pdf
        6 oz container, 2.5" dia x 2.75" height,  $0.48 ea, 36 to a case.
            https://www.uline.com/PDF/RS-14507-SPFR.pdf

    What's the difference between polypropylene vs polystyrene?
    Both are offered from Uline.  Polystyrene is clear, polypropylene is translucent white.
    I wonder how the polystyrene will accommodate drilled holes?
    Will polystyrene accommodate stress from volume potentiometer?

---Switches for Smart Amp?------------------------------------------------------

    This is way harder then it should be.
    	   inexpensive three way momentary switch, with three pushbuttons in the
           assembly.  $1.88 each.  Digikey PN: CKN10836-ND  Mfgr PN: PS-32C02-F NS
           The function is good for us, the mounting is horrible.  No go.

    Digikey, Switches, Rocker Switches,
    Filter for "In Stock" and Switch Function = "Mom-Off-Mom",
    then sort by price.

---GliaX Open Source Stethoscope------------------------------------------------

    https://github.com/GliaX/Stethoscope

    Models here:
    https://www.thingiverse.com/thing:2826304

    London, Ontario
    Tarek Loubani
    tarek@tarek.org
    https://glia.org

    White paper:
    https://journals.plos.org/plosone/article?id=10.1371/journal.pone.0193087
    Validation of an effective, low cost, Free/open access 3D-printed stethoscope
        Alexander Pavlosky, Jennifer Glauche, Spencer Chambers, Mahmoud Al-Alawi,
        Kliment Yanev, Tarek Loubani

    Research article on the GilaZ Open Source Stethoscope.

    And the magic words from that paper...

    Numerous groups have previously attempted to standardize methods to determine
    the efficacy of acoustic stethoscope models[2,16–20], but currently no accepted
    standardized modality exists. Consequently, the performance of any acoustic
    stethoscope is little more than the manufacturer’s claim or the subjective
    opinion of the user. Some groups have attempted to objectively compare acoustic
    stethoscope models and currently two competing methods of measuring frequency
    response exist. The first method uses air coupling to transmit frequencies[2–4,16,17]
    while the other uses a phantom to simulate vibrations of the chest wall[19,21,22].
    These methods allow investigators to quantitatively compare the sensitivity
    of a stethoscope model compared with another.

    Acoustic transfer

    The frequency response of Glia model stethoscopes, compared with the Littman
    Cardiology III, was determined using an experimental setup modeled from a
    phantom-based frequency response setup previously described[19]. A latex
    balloon filled with 2 L (2000 g) of water was used as a phantom and each
    stethoscope was applied to the surface by hand. Phantom excitations were
    supplied by an external vibrating speaker which was placed in contact with
    the balloon and sound was played at 86 Hz intervals between 0 and 5000 Hz
    (white noise) for 15 seconds. The output of each stethoscope was recorded by
    a microphone which was placed in a silicon tube attached to the stethoscope
    head for spectral analysis. Spectral analyses such as these have been used
    successfully in the past to analyze breath sounds recorded from individuals
    with lung pathology[40]. The simplicity of this design was intended to allow
    other users to validate our design independently.

    Gosh, I think that means we can obtain a quantifiable measurement between our
    different design proposals.  And that is really great news.  Anybody have an
    exciter speaker (blue tooth box you set on a desk, and the whole desk vibrates
    with your audio output?)

    From: https://github.com/GliaX/Stethoscope/blob/master/testing/Stethoscope_Validation.md
    In the above topology, the balloon contains 2L of water (2000g), acoustic
    input is supplied via a pair of Monster DNA headphones and sounds were
    recorded using a Hama microphone. Audacity was used to create a 15 second
    audio clip of white noise which was played through the setup with the output
    of each stethoscope being recorded for spectral analysis. The spectrum produced
    by each stethoscope model was then compared to that of the Littmann Cardiology
    III. These plots are shown below...

    https://www.ncbi.nlm.nih.gov/pmc/articles/PMC5851543/
    Validation of an effective, low cost, Free/open access 3D-printed stethoscope
    There are a lot of valuable links at the end of this paper.

    Other related notes and thoughts:
    https://github.com/GliaX/Stethoscope/issues/51
    -- I've found that the diaphragm should have a thickness of around 0.7-0.9 mm
       and should be made of a relatively hard plastic material for optimal
       performance. I ended up using a A4 paper folder from here:
       https://www.jula.se/catalog/hem-och-hushall/kontor/kontorsmaterial/document-storage/mapp-001996/

    https://github.com/GliaX/Stethoscope/issues/37
    -- If you can get a hold of X Ray film, that should be about the right thickness
       that was used in the very first stethoscopes. If you have a littmann diaphragm
       available to you, you can cut it and use it as a standard to compare.
    -- as for attaching the membrane, you should be able to just drop it into the
       printed ring and friction-fit the head into it. I haven't seen or encountered
       anything to suggest otherwise.

    https://github.com/GliaX/Stethoscope/issues/33
    -- ...nowhere do I see the diameter of the Diaphragm.  Is it supposed to sit
       inside the lip on the top of the head ?  Does it extend to the inner edge
       of the ring ?  Should it be glued to the lip, or does it need to have some
       play between the lip and the ring ?
    -- Short answer: 40mm diameter. (Apparently early versions had a rubber
       o-ring under the membrane...)

    https://github.com/GliaX/Stethoscope/issues/28
    -- Slot in O-ring
    -- https://www.theoringstore.com/index.php?main_page=index&cPath=367_98
    -- Here, they call them "Square Orings also known as Tetraseals® or lathe-cut rings - Buna-N -Duro 70".
    -- https://www.ecstuning.com/b-genuine-porsche-parts/thermostat-o-ring/94410692908/
    -- https://agenaastro.com/ahs-o-ring-2.html

    Alternate Version:   https://www.thingiverse.com/thing:2895115
    -- My stethoscope has rounder edges for improved patient comfort, as well as
       easier build plate removal.
    -- I widened the "spring" to reduce clamping pressure in the users ears.
       There are two models of the spring. I'd print the non-tight one first. It
       should be great for most people.
    -- I redesigned the chest piece in two versions.  One that is low profile with
       no supports.  One that adds a finger button to allow it to be easily held
       between the fingers Both chest pieces have rounded sound channels to reduce
       obstructions for better sound transfer.
    -- Diaphragm: 40mm diameter cut from a report cover with approx 0.35mm plastic sheet
    -- I have designed the chest piece so that the membrane (report cover) is
       held in place by pressure from the TOP and BOTTOM, NOT the sides! Make sure
       that when you cut the diaphragm out, it drops in to the ring without forcing
       it in. If you force it, it will per-tension the diaphragm and reduce it's
       sensitivity. It should drop in to the ring and then the ring gets squeezed
       down on to the chest piece. The diaphragm should lay completely flat with
       no bulges at all.

    Alternate Version:  https://www.thingiverse.com/thing:577507

    Stethoscope Head Design details?
        Start with source_files\scad\stethoscope_head\lib\printed\stethoscope_head.rb
        It looka like Ruby pushes content into SCAD.

---FabLab 3xD open source Stethoscope-------------------------------------------

    https://www.youmagine.com/designs/stethoscope-chestpiece

---ESP32 Power Off Info---------------------------------------------------------

    From: Ruthvik Bandaru
    https://lastminuteengineers.com/esp32-sleep-modes-power-consumption/

---Existing Electronic Stethoscope----------------------------------------------

    From: Ganesh
    https://stethome.com/

---Onshape Cad info on Covid Projects-------------------------------------------

    https://www.onshape.com/covid-19-support#participating-projects

---Notes on Solidworks Speaker Grill--------------------------------------------

    Add holes for speaker grill in nice pattern:

    https://help.solidworks.com/2018/english/SolidWorks/sldworks/HIDD_DVE_VENT.htm

    https://blogs.solidworks.com/solidworksblog/2012/08/solidworks-fill-pattern.html

    WTF?  The vent cannot be created due to failed geometry.  The normal vector
    from the center of the vent sketch must: intersect the face where you are
    placing the vent.  Penetrate INTO the selected face to calculate the vent
    depth.

---Screwboss in 3d printed parts?-----------------------------------------------

    http://infocenter.3dsystems.com/bestpractices/mjp-best-practices/projet-mjp-2500/fastening-screws-and-injection-molded-bosses
    https://blog.adafruit.com/2014/11/27/adding-screw-threads-to-3dp/
    https://all3dp.com/2/3d-printing-threads-and-screws-all-you-need-to-know/

    https://www.reddit.com/r/3Dprinting/comments/bq6cy9/3d_printed_screw_holes/
    https://www.thingiverse.com/thing:3639095

    Screws of interest:  17/32 19mm long, major dia 4.7mm, minor dia = 3.0mm
    lets try 3.6mm for hole id?

---Potentiometer Knobs----------------------------------------------------------

    https://www.thingiverse.com/tag:potentiometer_knob
    https://www.thingiverse.com/tag:volume_knob
    https://www.thingiverse.com/thing:2329397
        MP Select Mini V2 - Replacement Knob
        by makerboz May 18, 2017
    https://grabcad.com/library?query=potentiometer%20knob
    https://www.thingiverse.com/thing:199414

---Potentiometer Mounting-------------------------------------------------------

    Hole I.D. = 7.5mm
    Material Thickness at mounting (to ensure best strength, all threads used)
    = 2.6mm thick

    soldering aid?
    https://forum.digikey.com/t/does-digikey-sell-a-0-1-pin-socket-connector-set/6235

    These will likely work:
    https://www.digikey.com/product-detail/en/molex/5600230448/WM16315CT-ND/6702303
    https://www.molex.com/pdm_docs/sd/5600230448_sd.pdf

    Dupont Connectors
    https://www.plusivo.com/home/31-plusivo-dupont-connector-kit.html

---Audio Filters----------------------------------------------------------------

    https://en.wikipedia.org/wiki/Audio_filter
    https://en.wikipedia.org/wiki/Low-pass_filter

    https://www.electronics-tutorials.ws/filter/filter_2.html
        Passive Low Pass Filter

    https://www.electronics-tutorials.ws/filter/filter_5.html
        Active Low Pass Filter

    https://www.analog.com/media/en/training-seminars/tutorials/MT-222.pdf
        Sallen-Key Filters
        by Hank Zumbahlen,
        Analog Devices, Inc.

    http://www.dspguide.com/filtexam.htm
    The Scientist and Engineer's Guide to Digital Signal Processing
        By Steven W. Smith, Ph.D.

        See image of an analog low-pass filter
        6 pole Chebyshev, 6% ripple, 1.0kHz cutoff

    http://www.dspguide.com/ch3/4.htm
        Figure 3-8 shows a common building block for analog filter design, the
        modified Sallen-Key circuit. This is named after the authors of a 1950s
        paper describing the technique. The circuit shown is a two pole low-pass
        filter that can be configured as any of the three basic types. Table 3-1
        provides the necessary information to select the appropriate resistors
        and capacitors. For example, to design a 1 kHz, 2 pole Butterworth filter,
        Table 3-1 provides the parameters: k1 = 0.1592 and k2 = 0.586. Arbitrarily
        selecting R1 = 10K and C = 0.01uF (common values for op amp circuits), R
        and Rf can be calculated as 15.95K and 5.86K, respectively. Rounding
        these last two values to the nearest 1% standard resistors, results in
        R = 15.8K and Rf = 5.90K All of the components should be 1% precision or
        better.

        The particular op amp use isn't critical, as long as the unity gain frequency
        is more than 30 to 100 times higher than the filter's cutoff frequency.
        This is an easy requirement as long as the filter's cutoff frequency is
        below about 100 kHz.

    Q-Factor
        https://en.wikipedia.org/wiki/Q_factor
        Q factor is a dimensionless parameter that describes how underdamped an
        oscillator or resonator is. It is defined as the ratio of the peak energy
        stored in the resonator in a cycle of oscillation to the energy lost per
        radian of the cycle.  Higher Q indicates a lower rate of energy loss and
        the oscillations die out more slowly. A pendulum suspended from a
        high-quality bearing, oscillating in air, has a high Q, while a pendulum
        immersed in oil has a low one. Resonators with high quality factors have
        low damping, so that they ring or vibrate longer.

        For an electrically resonant system, the Q factor represents the effect
        of electrical resistance.

---OPAmp Design Notes-----------------------------------------------------------

    Op Amp gain of 100 which is 100x input signal. That would be 40 db amplification.

    Gain = 1 + Rf/Rin
    https://en.wikipedia.org/wiki/Gain_(electronics)

    How can I add gain to a Sallen-Key filter?
    https://electronics.stackexchange.com/questions/74877/gain-in-sallen-key-filter

    http://www.ti.com/lit/an/sloa024b/sloa024b.pdf
    Texas Instruments -- Analysis of the Sallen-Key Architecture

    https://www.electronics-tutorials.ws/filter/sallen-key-filter.html
        Pretty easy to understand description of what's going on...

    https://en.wikipedia.org/wiki/Sallen%E2%80%93Key_topology
        Lots of links to online tools to help out with design on this stuff.

    http://sim.okawa-denshi.jp/en/OPseikiLowkeisan.htm
        Sallen-Key Low-pass Filter Design Tool
        This page is a web application that design a Sallen-Key low-pass filter.
        Use this utility to simulate the Transfer Function for filters at a given
        frequency, damping ratio ζ, Q or values of R and C. The response of the
        filter is displayed on graphs, showing Bode diagram, Nyquist diagram,
        Impulse response and Step response.
        http://sim.okawa-denshi.jp/en/Fkeisan.htm
        http://sim.okawa-denshi.jp/en/OPstool.php
        (max gain appears to be limited, based on Q factor or Damping Ratio)
        Damping ratio of 1, max gain is 15.
        Q factor of 0.707, max gain is approx 1.5.
        First stage Gain = 15,
            R1 = 75kΩ
            R2 = 10kΩ
            R3 = 13kΩ
            R4 = 180kΩ
            C1 = 0.0015uF
            C2 = 0.022uF
        Second Stage Gain = 17.8/15.0 = 1.19
            R1 = 16kΩ
            R2 = 33kΩ
            R3 = 43kΩ
            R4 = 8.2kΩ
            C1 = 0.0068uF
            C2 = 0.0068uF

    https://www.youtube.com/watch?v=RexQOQnNmjc
        Sallen-Key 101: Gain and Attenuation
        Jun 23, 2014    Analog Devices, Inc.
        If you are going to add gain and you have a multistage filter, add the
        gain in the first stage...

    https://www.youtube.com/watch?v=DEV7l66D6Ys
        Filtering 101: Multi Pole Filters with Sallen-Key
        Jul 13, 2011    Analog Devices, Inc.

    https://www.youtube.com/watch?v=DUC389esZdM
        Filtering 101: Sallen-Key vs. Multiple Feedback
        Jun 23, 2014    Analog Devices, Inc.

    https://www.youtube.com/watch?v=FGbm4HUzUwk
        66. Low Pass Active Filters
        Jan 9, 2018    The Offset Volt
        59:43, long video, but seems well done.
        This guy sounds like Mr. Rogers, welcome to the neighborhood
        Filter review: Bessel, Butterworth, Chebyshev, Elliptic
        Butterworth, flat response, but, phase issues that affect audio signals.  Not recommended.

    https://blog.bliley.com/filter-typology-face-off-a-closer-look-at-the-top-4-filter-types

    http://www.tedpavlic.com/teaching/osu/ece327/lab7_proj/lab7_proj_procedure.pdf
        good notes within this document
        As you will see, Butterworth filters have maximally flat amplitude response
        in the passband. Unfortunately, they have two major drawbacks.
        --Poor Roll-off: Butterworth high-frequency roll-off is shallow, which means
          that high-frequency signals are not greatly attenuated. To remedy this,
          our power amplifier has provide an additional high-frequency pole.
        --Poor Phase Response: Butterworth low-pass filters have extremely poor
          phase response near the corner frequency. The non-linear phase response
          delays some frequencies more than others. The result is that inputs with
          significant high-frequency components are distorted on the output because
          their higher-frequency components are re-combined out of phase.
        Together, fast inputs to your circuit may be significantly distorted after
        smoothing.

    https://tools.analog.com/en/filterwizard/
        Analog Filter Wizard

    Reminder:
        y = log-base-a (x)
        So that --> a^y = x

        e.g.
        log-base-10(10^7) = 7

    If we want a total voltage gain of 100..

    current Adafruit amp max = 18db = 20Log-base-10 (Vout/Vin)
    Vout/Vin ==> 7.94
    current Adafruit amp max = 15db = 20Log-base-10 (Vout/Vin)
    Vout/Vin ==> 5.62

    We want 100!     100/7.94 = 12.6        100/5.62 = 17.8
    db = 20 Log-base-10(12.6) = 22db
    (i.e. we need this much pre-amp gain to get V/V Gain of 100)
    18db + 22db = 40db
    db = 20 Log-base-10(17.8) = 25db
    18db + 25db = 43db

    Can we get a multiple stage Sallen-Key filter to provide 22db of gain at the
    input to the audio amp?

    OpAmp Slew Rate?
        https://forum.digikey.com/t/suitable-slew-rate-in-op-amp-circuit-design/641
        Slew rate reflects the output voltage conversion rate of the Op amp. In
        other words, it shows how fast the Op amp can respond to a rapid change
        of input level.

    Here's an interesting dev board from digikey.
    https://github.com/sparkfun/OpAmp_Breakout-LMV358/tree/V_1.6
    1568-1278-ND  BOB-09816	SparkFun Electronics	SPARKFUN OPAMP BREAKOUT - LMV358	$5.50000

    https://www.digikey.com/products/en/integrated-circuits-ics/linear-amplifiers-instrumentation-op-amps-buffer-amps/687
    OpAmp sort: On hand, Mounting Type: thru-hole, Voltage - Supply, Single/Dual (range 1v ~6v and all combos of that...)
    MCP6002-E/P-ND   MCP6002-E/P	Microchip Technology
    IC OPAMP GP 2 CIRCUIT 8DIP	$0.36000
    http://ww1.microchip.com/downloads/en/DeviceDoc/MCP6001-1R-1U-2-4-1-MHz-Low-Power-Op-Amp-DS20001733L.pdf

---Capacitor notes--------------------------------------------------------------

    Ceramic or Aluminum Electrolytic or Film or Tantalum or Aluminum Polymer...

    use the generic rule that if it is under 1uF go with ceramic, over iuF get electrolytic.

    https://electronics.stackexchange.com/questions/70545/film-or-ceramic-capacitors-for-op-amp-feedback-bw-limit

    https://www.digikey.com/products/en/capacitors/ceramic-capacitors/60
    Filter: In Stock Filter: mounting type - Thru Hole

---ESP32 and Audio--------------------------------------------------------------

    https://www.youtube.com/watch?v=SCAKQsGt9wI
    ESP32 .WAV File Playback | PAM8302 Audio Amplifier
    Sep 22, 2019    ACROBOTIC

    https://www.hackster.io/julianfschroeter/stream-your-audio-on-the-esp32-2e4661
    Julian -- Published March 6, 2018 © GPL3+
        Stream Your Audio on the ESP32
        Use the ESP32 to play audio data from a custom stream.

---Voltage Regulator------------------------------------------------------------

    For analog design, quick and dirty, a simple voltage divider is a choice.
    downside? loss of voltage minimum when batteries start to die.

    https://en.wikipedia.org/wiki/Voltage_regulator#Linear_regulators

    voltage regulator?
    https://en.wikipedia.org/wiki/Voltage_regulator
    A simple linear voltage regulator should do the trick.
    Filter: In Stock, Thru Pin, 2V thru 2.5v.  Sort by price.
    MCP1700-2502E/TO-ND     MCP1700-2502E/TO	Microchip Technology	IC REG LINEAR 2.5V 250MA TO92-3  $0.37

---Electronics References-------------------------------------------------------

    The Art of Electronics, by Paul Horowitz and Winfield Hill

    https://www.analog.com/en/education/education-library/practical-design-techniques-sensor-signal-conditioning.html
        Practical Design Techniques for Sensor Signal Conditioning, 1999
        Edited by Walt Kester, Analog Devices, 1999, ISBN-0-916550-20-6.

---Microphone pickup using hoses and nipples?-----------------------------------

    hose?
    GliaX Stethoscope hose:
    40cm - 50cm Silicone 13mm (preferred) or 12mm OD, 8mm ID, 50 durometer
    8MM I.D X 13MM O.D NGP60 Clear Translucent Silicone Hose Pipe Tubing (USD$7.34/meter)

    LBC notes:
    I have 6.5mm ID stiff poly hose / 9.6mm O.D.
    I have 8.5mm id soft clear vinyl hose

---Battery Holder---------------------------------------------------------------

    Wow, Digikey has lots and lots of parts here... including springs and contacts,
    so a shaped battery holder is totally possible.

    https://www.digikey.com/products/en/battery-products/battery-holders-clips-contacts/86?k=battery%20holders
    three cell AA holder = $1.61
    There are a ton of clips and springs available there to design your own.

---DIY Boards-------------------------------------------------------------------

    https://oshpark.com/

    Er, wait.. if we do a custom board, why bother with Adafruit class d audio amp?
    can we find something we can solder?

    how to?

    https://www.youtube.com/watch?v=_3jFsNffzxQ
    How to Make a Custom PCB - Part 1 - Making the Schematic
    Jun 27, 2016        Circuit Basics

    https://www.youtube.com/watch?v=g4iiekExXak
    How to Make a Custom PCB - Part 2 - Making the PCB
    Jun 27, 2016        Circuit Basics
        https://www.circuitbasics.com/make-custom-pcb/

---hand soldering?--------------------------------------------------------------

    https://jeelabs.org/book/1513c/
    Soldering a TSSOP chip by hand

    https://forum.sparkfun.com/viewtopic.php?t=18125
    TIPS FOR SOLDERING SSOP PINS

    https://www.digikey.com/products/en/integrated-circuits-ics/linear-amplifiers-audio/742
    thru pin?  (not likely for 3v to 6v power)
    Supplier Device Package: X-SOP, X-MSOP, X-SOIC, X-VSSOP, X-Multiwatt, PowerSSO-X, X-TSSOP, X-HTSSOP
    filter parameters:
    voltage Supply:
    in stock: check
    View Prices at: 1

    Alternatives, toaster oven (reflow), Hot plate reflow.

---Fritzing---------------------------------------------------------------------

    Breadboard Layout?
    https://fritzing.org/home/

    Fritzing is an open-source hardware initiative that makes electronics accessible
    as a creative material for anyone. We offer a software tool, a community website
    and services in the spirit of Processing and Arduino, fostering a creative
    ecosystem that allows users to document their prototypes, share them with
    others, teach electronics in a classroom, and layout and manufacture professional
    pcbs.

    https://fritzing.org/download/
    They are asking for a donation of $9 for each download.

    https://github.com/fritzing/fritzing-app
    https://github.com/fritzing/fritzing-app/wiki

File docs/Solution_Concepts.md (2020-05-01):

These solution ideas are mainly to see what sorts of things would work *practically* in a hospital environment.

### Problems with current stethoscope solution: ###
  - Stethoscopes are expensive and hard to disinfect, resulting in a situation where cheap, disposable stethoscopes are often left with
      a single patient for the duration of their stay (in developed countries). 
  - Disposable stethoscopes are low-quality (poorer sound).
  - Disposable stethoscopes wear out quickly.
  - Disposable stethoscopes are quite short, forcing the doctor closer to the patient, and for a longer time, than necessary.
  - A doctor in PPE gear like this will have a hard time getting a stethoscope into their ears.

### The goals for the "stethoscope" are: ###
  - A doctor needs to hear a patient's lungs and heart in a hospital setting.
  - This needs to be easily functional while the doctor is fully dressed in PPE.
  - Easily sterilizeable.
  - Made of parts we can source to make a sizeable quantity.
  - Get it done - as quick a turnaround as possible.
  
  Mike Vang's notes from 3/29/20 meeting:
  - Pick up sound range between 20Hz to 1kHz.
  
### Design constraints: ###
  - Allows the medical professional to maintain at least arm-length distance, and be easy to use while intubating.
  - Relatively inexpensive.  Such as, in the range where parts of the device(s) that come in contact with the patient
    are effectively disposable.
  - Easily sterilizeable, or be placed in a container/wrapping that is easily sterilizeable while still functioning.
  - Durable, able to handle many sterilization cycles without degrading.
  - A battery life sufficient to handle a 10-hour shift.
  - Dead simple to configure, as few failure points as possible.

### Other: ###
- If something works or doesn't work in the hospital setting currently, there's probably a really good reason for it.
- Don't re-engineer anything we don't have to.

### Questions for Brian: ###
- Could you tell us about your experience with the proof-of-concept device you sent a picture of?  What works or doesn't work about that?
- Do hospitals deal well with things that require batteries or charging?  Would it be better if the puck/microphone device could be
  plugged in and left on/near the patient as part of the station?
- Do doctors regularly use phones/tablets for per-patient equipment in emergency situations? In other words, are there existing
  phones/tablets in this environment already that we could use to pair with a cup/puck and headphones?
- Can a standard off-the-shelf Ziploc sandwich bag be used as a quick-and-dirty disposable sterilizeable protective shield on the device between patients?
- Can a surgical rubber glove (tied in a knot) be used as a quick-and-dirty disposable protective shield on the device between patients?
- I assume that *someone* will need to get close enough to the patient to hold the device to different areas of the patient's 
  chest/back. Is that correct? Does that person need to be the doctor? How important is it really to have a wireless connection vs.
  an arms-length cable?
- Would the doctor desire to tape a cup/puck unit to the patient and leave it there to free up hands while listening?
- What do doctors currently use for pulse oximetry, and how is it sterilized between patients?
- Does the Doctor need both oximetry and lung audio info at exactly the same time?

Mike Vang's question:
- When working with a patient incubating covid-19 (test positive and can spread it; not familiar with medical jargon), which area around the patient is most dangerous? (I assume the a cone shape in the front of the patient.) And can you determine the shape & size of that area? I assume taking a patients breath from the back and taking a person's SpO2 reading, say from the side, is the safest for HCP's?

Feedback from Brian 3/29/20
Mike Vang's notes (addition and correction to these notes are welcomed):
  - One stethosocope throughout the day could be shared by multiple HCP (healthcare providers)
    - The ones who goes into the patient's room are more likely nurses than doctors.
      - Anyone who needs to listen to a patient's breathing could go into a room.
    - Sterilization lessens if there was one device per patient.
      - Issue: Will scaling for higher number of patients become an issue?
    - Stethoscopes are used about 30s to 1 min.
    - Brian has been sterilizing his stethoscope with alcohol.
    - Listening protocol is to lay patient on back with chin adjusted. Then listening is conducted.
      - Bags are sometimes placed over the patient's head to reduce exposure of covid-19 to HCP.

### Solution Space 1:   Quick and Simple and Dirty - Stethoscope Only ###

Why do we need headphones? The absolute simplest design would be a puck with a microphone, a battery-powered amp, and a speaker.
Lowest level of technology, more fool-proof, no configuration.  Could be taped in place while the patient is being intubated.
As long as the sound quality is acceptable for the doctor's use,  the doctor (and anyone else) wouldn't need headphones to hear.
Less equipment to charge, carry around, and sterilize.

Picture something like this, except smoother and flatter:

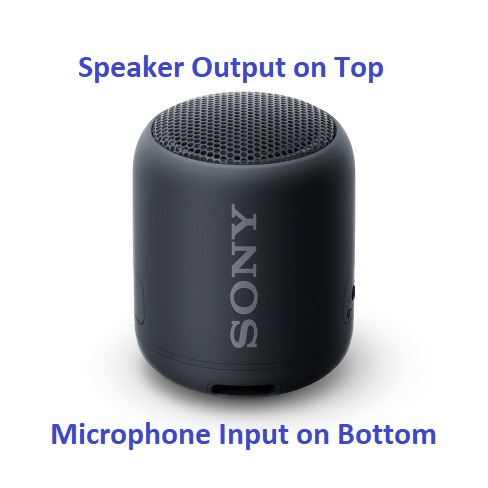
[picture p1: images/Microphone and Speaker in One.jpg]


Questions:
  - Would the sound level be acceptable in a hospital environment?  Or conversely, would a noisy hospital environment drown out the speaker?
  - Nonetheless, would this be a workable tradeoff for a dirt-simple, cheap solution?
  - What if these were used mainly during intubating, but we had a more traditional stethoscope-type solution for lower-stress procedures?

Mike Vang's comment:
  The more I think about simplifying an electronic stethoscope, an electronic stethoscope with a speak could be the ideal solution. Another issue I can come up with is can an HPC hear the breathing clearly while donning PPE?
  Also, a simple electronic stethoscope with a speaker could be v.1 while v.2 could add Bluetooth functionality?

### Solution Space 2:   Existing Stethoscope Solutions - Stethoscope Only ###

This is the Stemoscope:  https://www.stemoscope.com/

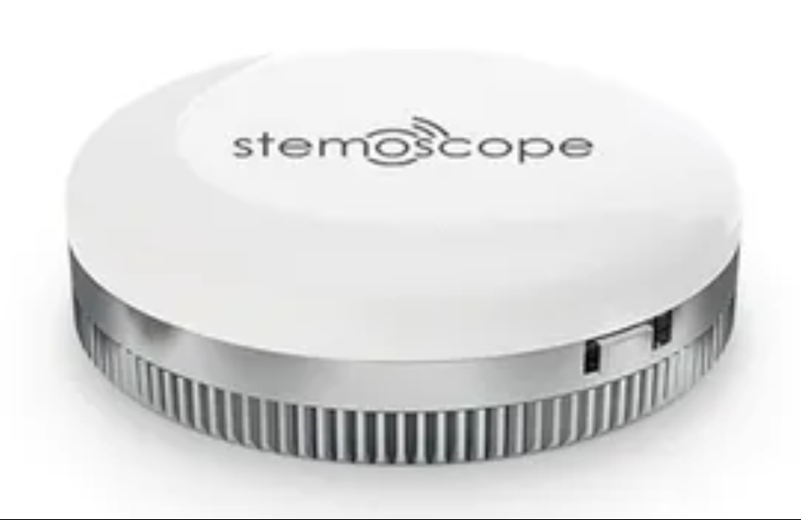
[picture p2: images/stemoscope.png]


It's functionally everything we want in a puck - picks up sounds with a good microphone and transmits them wirelessly to a
  headphone/speaker.  If we go the wireless headphone route we should absolutely use this if we can solve or waive the following issues:
- The current cover can't be effectively sterilized - too many slots and holes.  Would need to buy coverless and make new
    smooth/waterproof covers, or get the manufacturer to create a new design.
- It requires an expensive phone or device to be the master of the system and connect to both the puck and the headphones, for a total of 3 devices.
- More wireless connections == more configuration and more points of failure.
- Availability.

Pros:
- The most flexible option allowing for selection of different pucks and headphones.
- It physically exists as a current product.
- Software development is done.

Cons:
- Requires an addition device for use
  - iPhone, iPad, iPod Touch with iOS 7+ or Android 5.0+ with Bluetooth Low Energy (BLE) support
  - Headphones connect through device; headphones cannot connect directly to Stemoscope
- Stemoscope cannot pair

Questions:
  Instead of being sterilized, could it be enclosed in a plastic bag that could be sterilized?  Would this work in a hospital environment?
  
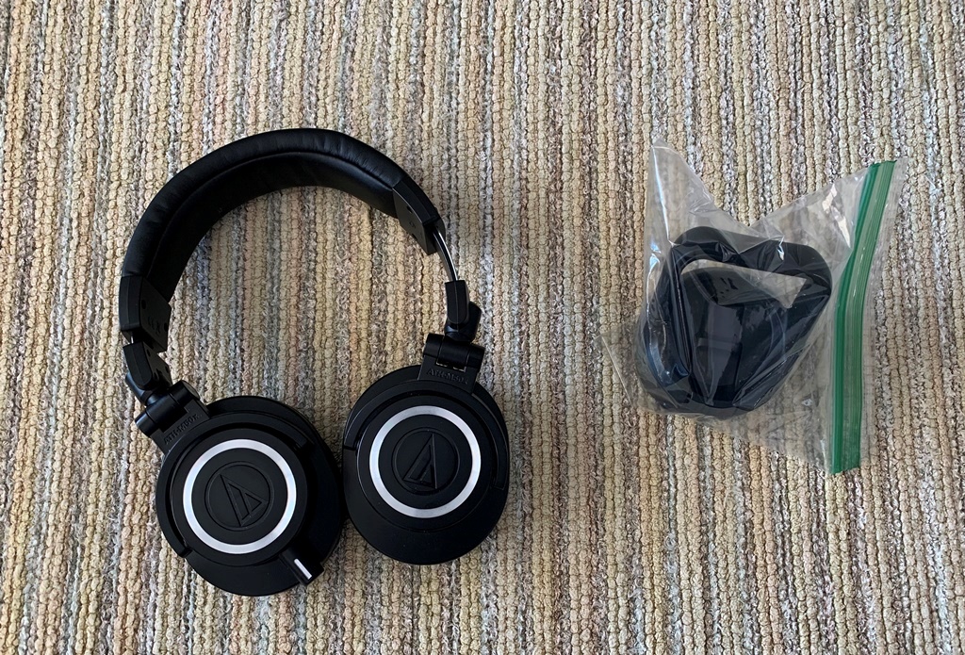
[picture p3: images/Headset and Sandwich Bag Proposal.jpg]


Notes:
  Michael Vang/mvang said they would contact Stemoscope to see about collaboration possibilities. (3/28)

### Solution Space 3:   Create Our Own Puck with integrated cup - optional Oximeter ###

If Stemoscope (or other similar option) doesn't work, we can create our own puck.  The puck would master the system, connecting via
  a wireless link to a pair of headphones worn by the doctor.  It would likely need a small screen and a couple buttons to select/pair
  with the headphones.

Idea:  Create our own stethoscope puck that can be a bluetooth master.  There are existing [ESP32](https://smile.amazon.com/gp/product/B076KJZ5QM/ref=ox_sc_act_title_1?smid=A1N6DLY3NQK2VM&psc=1) controller boards that we could source
for development, and possibly even for production.  These contain a bluetooth master, a lithium battery controller, and a small screen
for ~$17 single-unit price plus some cost for an antenna - I assume we could get cheaper antennas than this.



Pros:
  Solution requires only the puck and headphones.
  
Cons:
  Custom solution - requires custom case and custom software development.
  
Could end up looking something like this, or maybe a more compact puck-shaped solution:
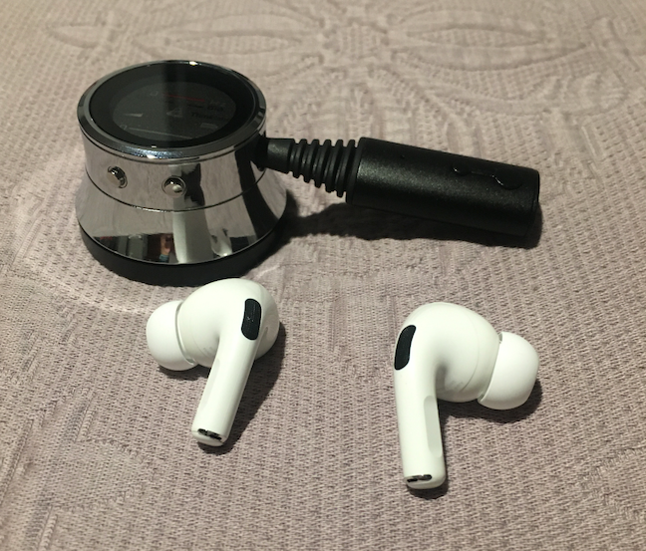
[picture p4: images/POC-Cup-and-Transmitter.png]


There are ESP32 microcontroller boards with built-in Bluetooth mastering that could be used, that come with a microphone and battery charging controller.  These could also control the reflective-mode oximeter logic if we go that route.

Mike Vang's comment:
  I was thinking about oximeter placement. What if the oximeter reader was placed on top of the puck/device?
  
  Also, I found an open-source Bluetooth Low Power stack here:
    https://mynewt.apache.org/

### Solution Space 4:   Reuse the stethoscope/cup - Stethoscope Only ###

Idea:  Use an existing stethoscope cup.  There are devices on the market that attach to the tube/cup of an
existing stethoscope, like this:

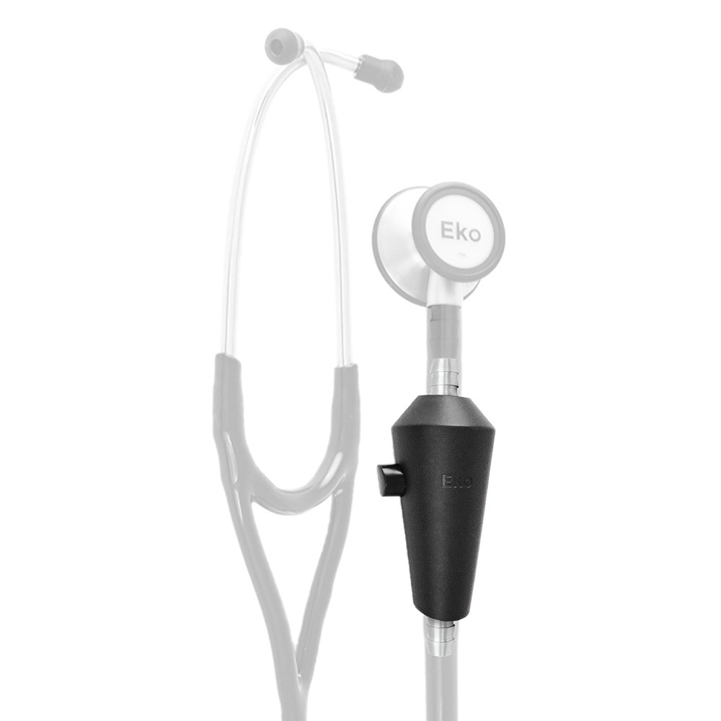
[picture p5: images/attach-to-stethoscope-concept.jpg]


They are, however, very expensive (that one is $200/unit).  If this general solution is workable, we could possibly negotiate with
  the company or create our own similar solution.

Pros:
  - This re-uses the tried-and-true stethoscope so we don't have to re-engineer.
  - Exists physically as an FDA-cleared product.
  
Cons:
  - Looks unwieldy, hard to operate with one hand?
  - Dependent on existing stocks of stethoscopes.

Optional:  We wouldn't even need the rest of the stethoscope.  We could use existing stethoscopes and just cut off the headpiece (although that's wasteful), or just source stand-alone stethoscope cups and attach our own tubes,

### Solution Space 5:   Puck with Integrated Blood Oximeter ###
 
Clarify the original problem statement/use models - we need more information about how having an integrated blood oximeter would work.  Would the doctor generally read the oximeter *while* listening to the patient?  Would the puck have a digital readout, or provide some audio queue?  Are there times when you would want to listen and use the oximeter on the patient at different sites at the same time?

Existing finger-clip oximiters on Amazon are around $20.  Are they too expensive, hard to disinfect, or why are these not a good hospital solution?  Do you know what models are currently in use?

This is a good article on relective-mode oximetry:  https://www.sciencedirect.com/science/article/pii/S2405959516301205

Apparently fingertip/earlobe oximetry is "transmissive mode" oximetry.  "Reflective mode" oximetry is possible at the wrists or other sites, so this could theoretically be integrated into a stethoscope puck. The hardware is different than transmissive-mode solutions, I don't see any commercially available.  The circuit doesn't look that hard, could possibly prototype using the ESP32 as the microcontroller:

From https://core.ac.uk/download/pdf/81961664.pdf, page 2:

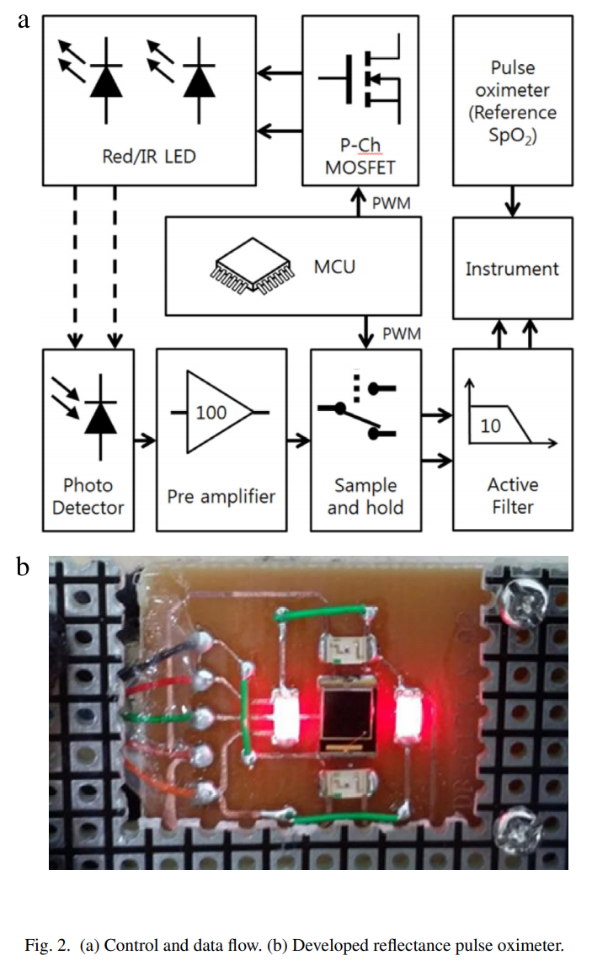
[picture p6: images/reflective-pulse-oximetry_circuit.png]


Mike Vang's comment:
  From what I have read so far, accuracy plays a significant role in how effectively a pulse oximeter can read SpO2 levels.  From the literature I have read, I concluded the optimal spots are the hands, wrists and/or fingers. 

### Other interesting data points:###
  - Cheap bluetooth converters are all over the market that let you plug in a pair of *wired* headphones.  Like [these](https://smile.amazon.com/APEKX-Bluetooth-Headphones-Wireless-Hands-Free/dp/B01MUXYVOA/ref=sr_1_3?crid=8LU8JAFJEWS0&keywords=bluetooth+adapter+headphones&qid=1585470679&sprefix=bluetooth+adapter+head%2Caps%2C211&sr=8-3):
  - There are reasonable-looking 3D-printer plans for stethoscopes, such as:  https://all3dp.com/3d-printed-stethoscope/
  - There are reasonable-looking 3D-printer plans for over-the-ear headphones, such as:  https://www.instructables.com/id/3D-Printed-Bluetooth-Headphones/

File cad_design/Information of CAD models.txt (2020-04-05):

---ESP32 Model------------------------------------------------------------------

    https://grabcad.com/library/heltec-wifi-lora-32-shield-1
    Heltec WiFi LoRa 32 Shield
    Raphael F. Martins
    February 3rd, 2020
    ESP32 / LoRa / WiFi/ Bluetooth/ OLED Display
    Manufacturer: Heltec
    SW2018

---AA Battery-------------------------------------------------------------------

    https://grabcad.com/library/energizer-double-a-battery-1
    Energizer Double A Battery
    Russell Watters
    July 13th, 2019

---Speaker----------------------------------------------------------------------

    http://www.puiaudio.com/pdf/AS04004PR-R.pdf
    Pui Audio, 3 watt, 4Ohm speaker, purchased from Digikey
    wow. PUI provides cad models. Awesome.

    Cad model comes from Digikey.
    https://www.digikey.com/product-detail/en/pui-audio-inc/AS04004PR-R/668-1359-ND/3189932
    The only file we can get is an .igs file

---Adafruit audio amplifier board-----------------------------------------------

    Double wow.  We're lucky this exists..
    https://grabcad.com/library/arduino-audio-amp-board-987-1
    Arduino Audio Amp Board 987
    In fact this guy is brilliant.  He place headers on both the top of and the
    bottom of the board. Pick what you need and hide the rest. Really great work.

    We made a separate copy with the hidden stuff deleted to deal with the import
    eccentricities of OnShape. Separate copy = "Arduino Audio Amp mAX98306 with pin mods"...

    davidrmillar
    May 19th, 2016
    Arduino Audio Amp Board MAX98306. Adafruit 987. This is a SolidWorks 2016
    Model. IGES and STEP files available.

---CUI Microphones--------------------------------------------------------------

    https://www.cuidevices.com/
    I can find CAD models of the mic's but not the prototype board.
        CMM-3312AT-44308-TR MIC5 MEMS analog top 3.3 -44 80  (MEMS, Omnidirectional)
        CMR-2747PB-A MIC6 ECM analog top 6.0 -47 500 (Electret, Noise Cancelling)
        CMC-6015-47P MIC7 ECM analog top 6.0 -47 500 (Electret, Unidirectional)
        CMC-4013-SMT-TR MIC8 ECM analog top 4.0 -42 500 (Electret, Omnidirectional)
        (last three #s above indicate dia(mm) Sensitivity(dB) Current (microAmps))

    each of the 4 pieces is a 0.59” x 0.59” square and the board thickness
    is 0.032”.

---Bourns Potentiometer Volume Adj----------------------------------------------

    https://www.bourns.com/resources/design-tools/engineering-files-list?Folder=PTR90

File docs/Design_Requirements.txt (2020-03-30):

This file is for discussions of product requirements and design decisions.  There are a number of different ways we could go with
this design depending on the use cases and requirements for both the stethoscope and pulse oximetry devices.  I would ask the
medical professionals to review assumptions and clarify.

From the original project description we have:
  -Inexpensive
  -Patient-contacting portions either need one device per patient, *or* need to be easily sterilized between patients, or both.
  -Avoid having to get/stay close to the patient if possible. (Bluetooth specified, but guessing any short-range wireless solution would do)
  -If possible, combine stethoscope and pulse oximetry.

Verbal conversation with Dr. Brian indicated that listening to a patients lungs while inserting a breathing tube is difficult with protective gear and a normal hose type stethoscope.  The doctor needs to be relatively close to the patient.

General usage questions:
  Is it important that the device conform to a traditional stethoscope format?  For instance, is it important that there be
  earpieces?  Would it work to create a battery-powered cup with a speaker on the back?  (A microphone, small amplifier and a
  speaker would be about the simplest design possible).  Do we need in-ear earphones, or would big over-the-ear-and-hood headphones
  be acceptable?  How noisy is the environment when this device will be in use?

  Will either a speaker or over the ears studio style headphones work with full protective gear, including hood without PPE removal?
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

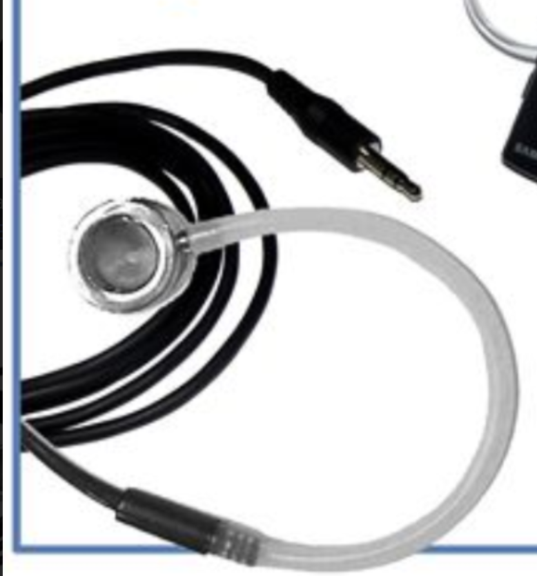
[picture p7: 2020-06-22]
docs/devkit/images/devkit_wand_concept_1.png

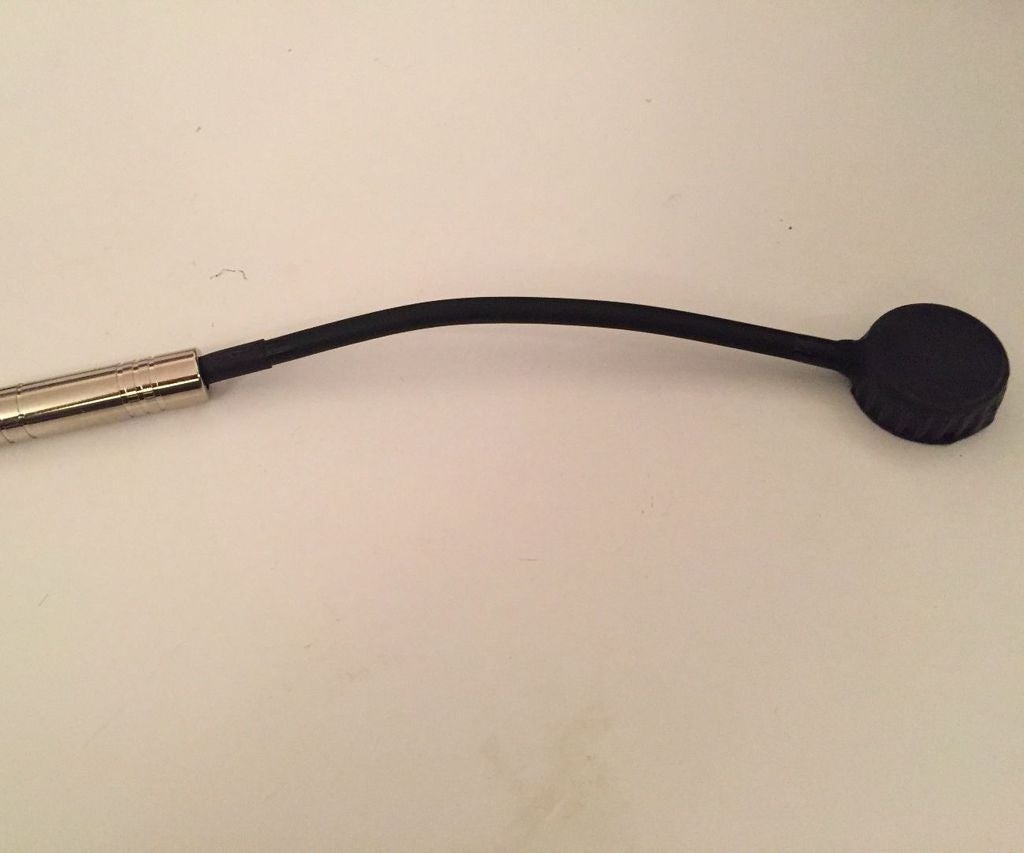
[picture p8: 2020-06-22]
docs/devkit/images/devkit_wand_concept_2.jpg

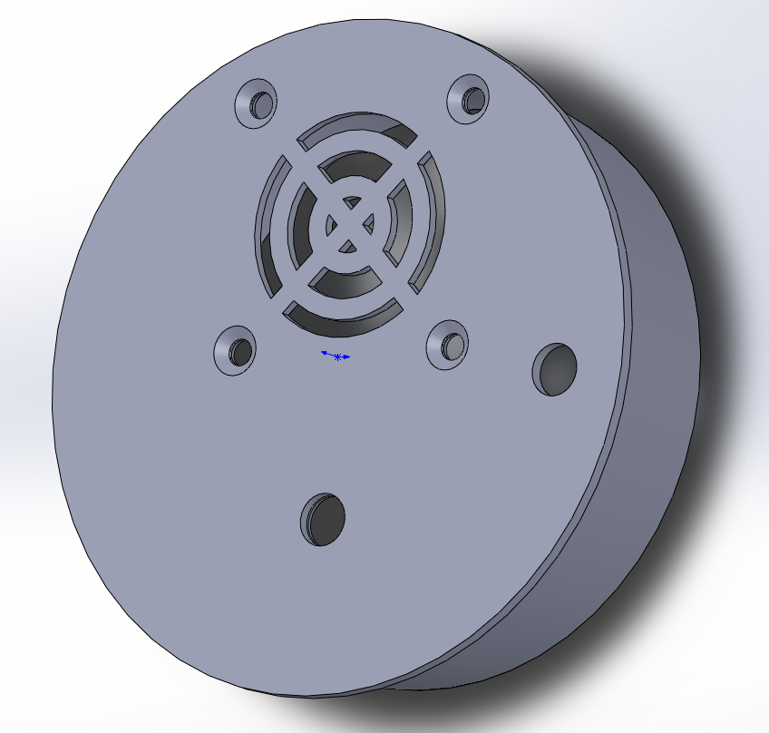
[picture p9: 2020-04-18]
cad_design/cap-for-16oz-cup/CapWithScrewHoles.png

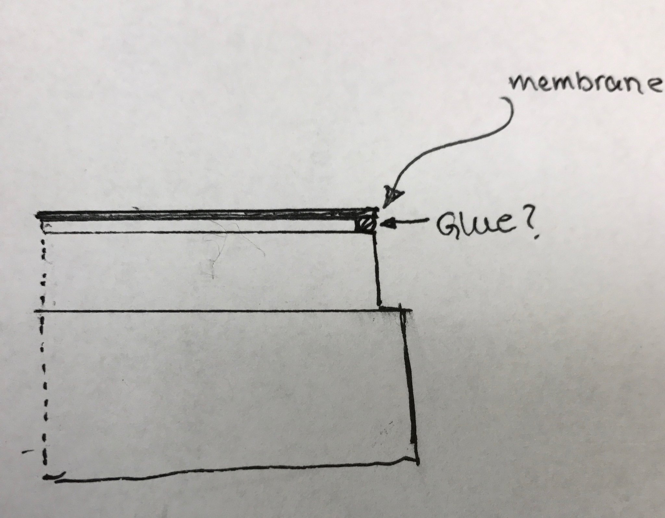
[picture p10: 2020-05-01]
cad_design/GliaX Stethoscope Use for Reference/S.Aquinaga_34860714690_f365ee9ff0_k.jpg

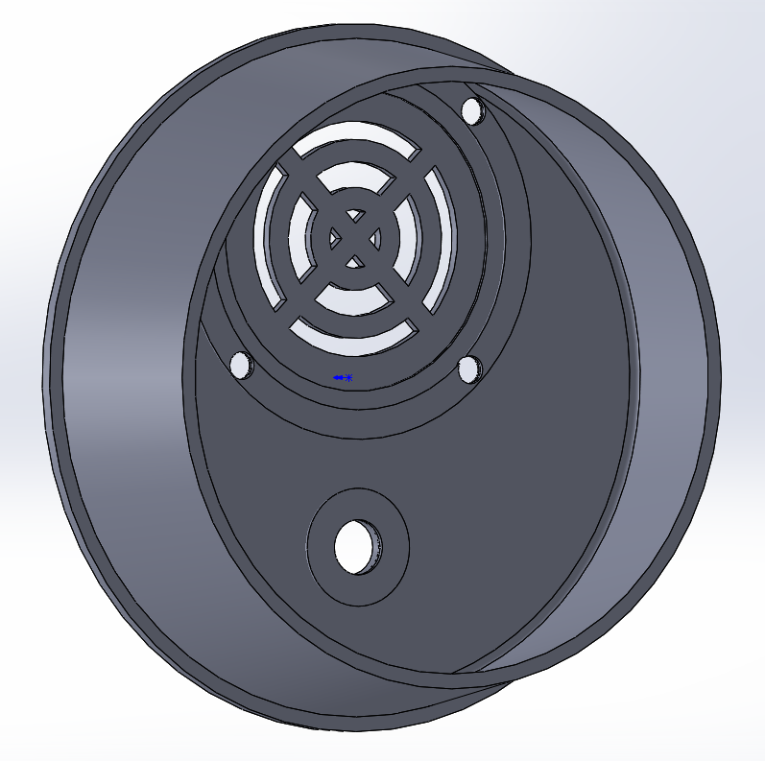
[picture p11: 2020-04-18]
cad_design/cap-for-16oz-cup/cap3.png

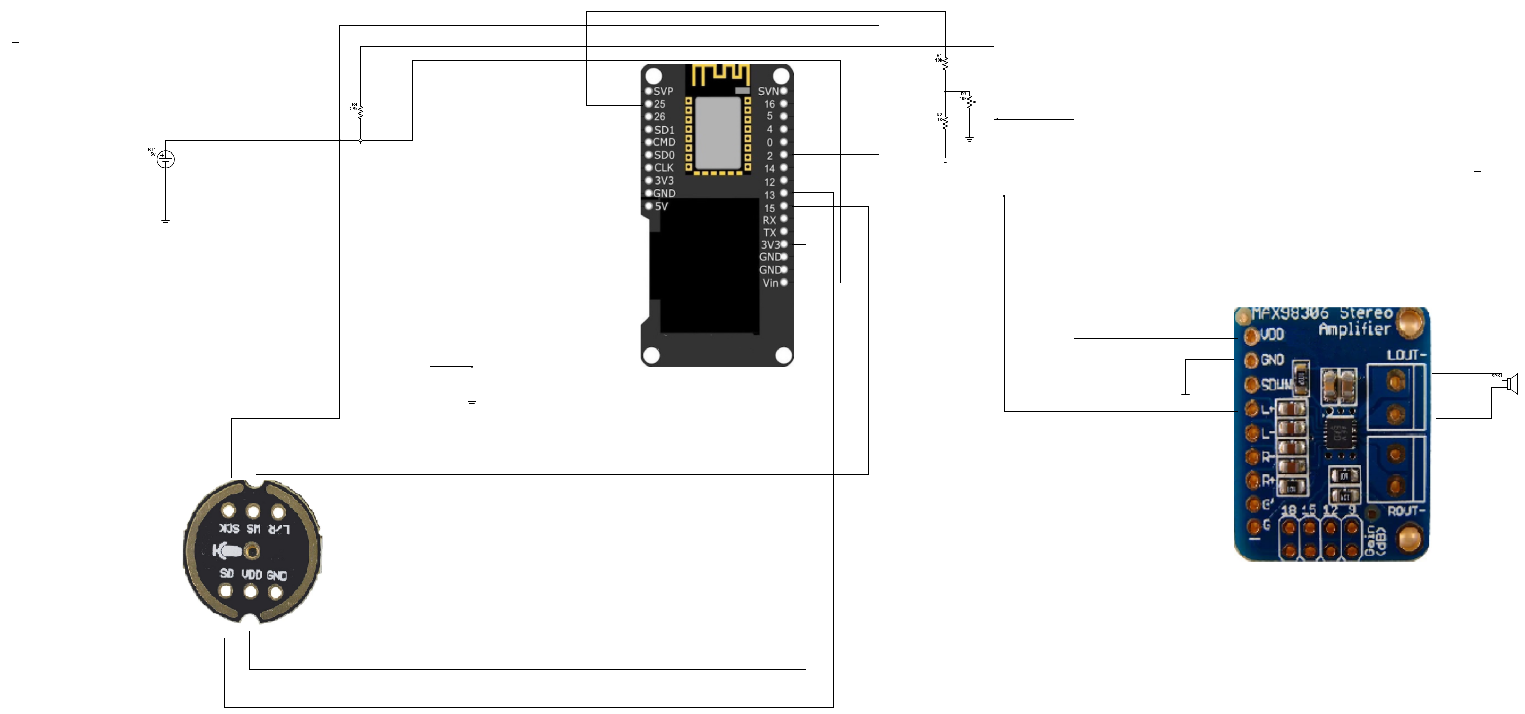
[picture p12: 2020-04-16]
electrical_schematics/schemeit-project (2).png

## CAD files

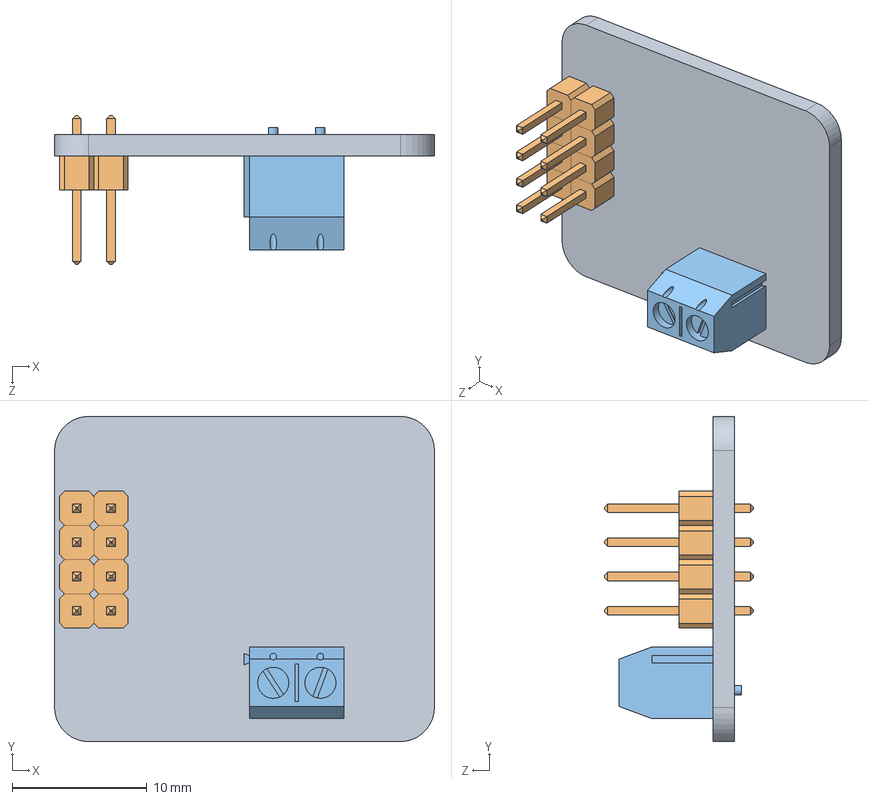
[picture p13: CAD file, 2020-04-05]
cad_design/adafruit-audio-amp/ARDUINO AUDIO AMP MAX98306 987 with pin mods.SLDASM
28.2 x 24.1 x 11.1 mm
ARDUINO AUDIO AMP MAX98306
.100 Header
Jack

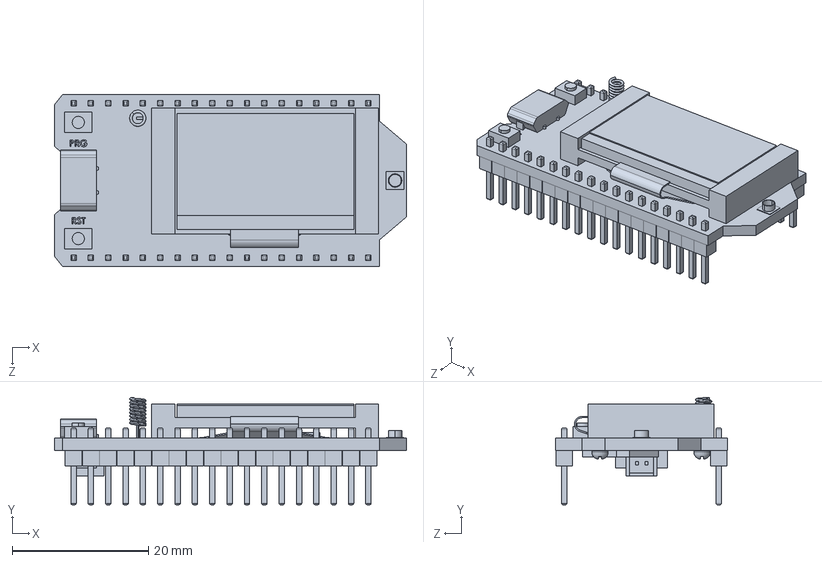
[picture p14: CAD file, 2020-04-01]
cad_design/esp32/heltec_wifi_32_asm2.SLDPRT
51.8 x 15.8 x 25.3 mm

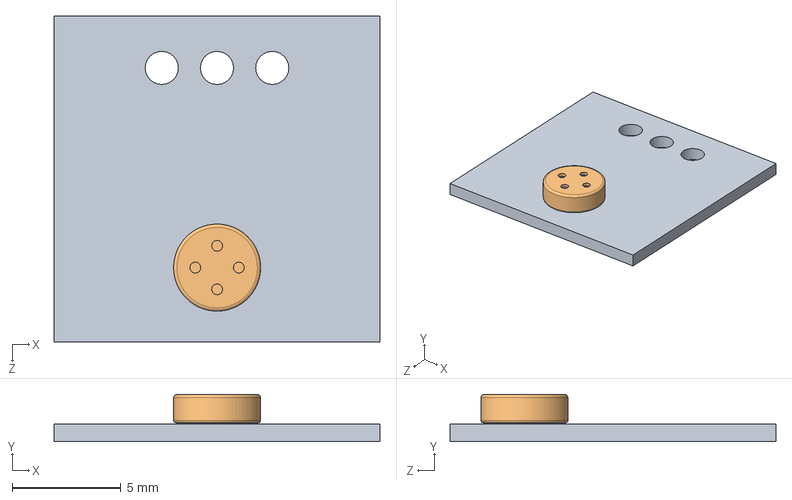
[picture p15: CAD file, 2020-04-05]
cad_design/microphone/Mic4013onBoard.SLDASM
15.0 x 2.16 x 15.0 mm
mic_board
CUI_DEVICES_CMC-4013-SMT-TR

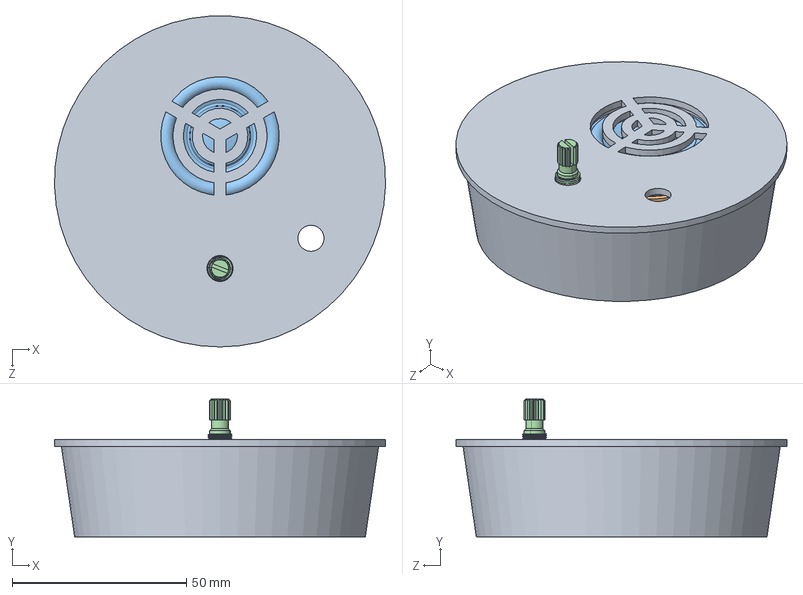
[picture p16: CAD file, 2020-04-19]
cad_design/quick-and-dirty-assy/QuickAndDirtyAssy.SLDASM
95.0 x 39.5 x 94.9 mm
cap-for-cup-v2
speaker-retainer-ring
Speaker AS04004PR-R
Volume Pot On Off ptr901-2x15k-xxxx

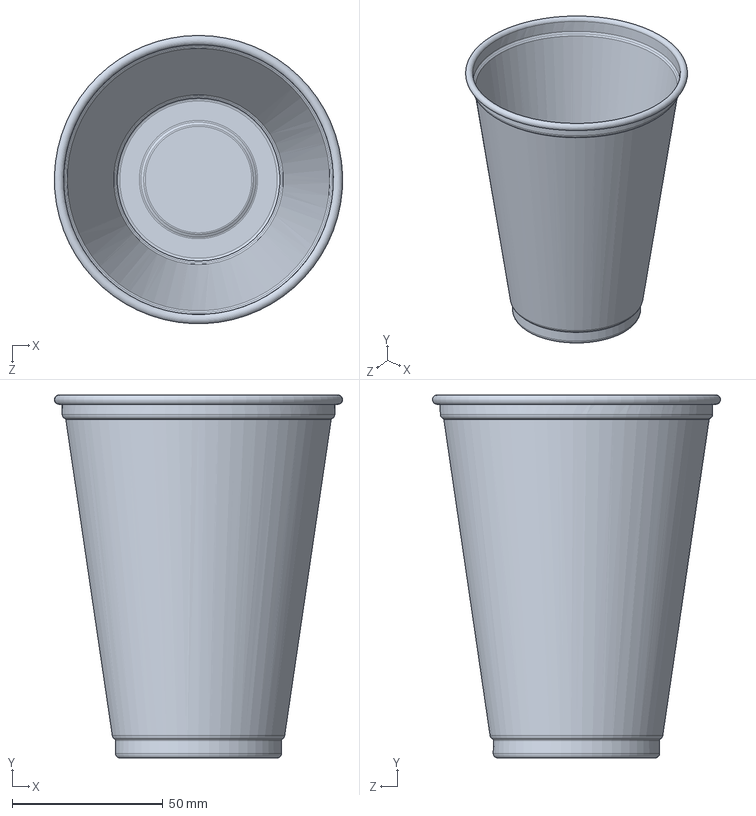
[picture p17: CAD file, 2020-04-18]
cad_design/16-oz-plastic-cup/16-oz-plastic-cup.SLDPRT
95.7 x 120.5 x 95.6 mm

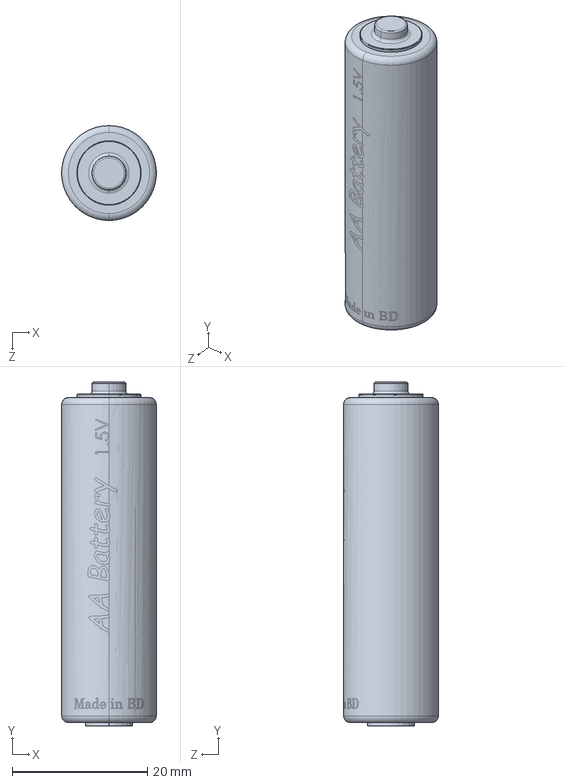
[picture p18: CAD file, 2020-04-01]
cad_design/aa-battery/aa_battery.SLDPRT
14.0 x 50.8 x 14.0 mm

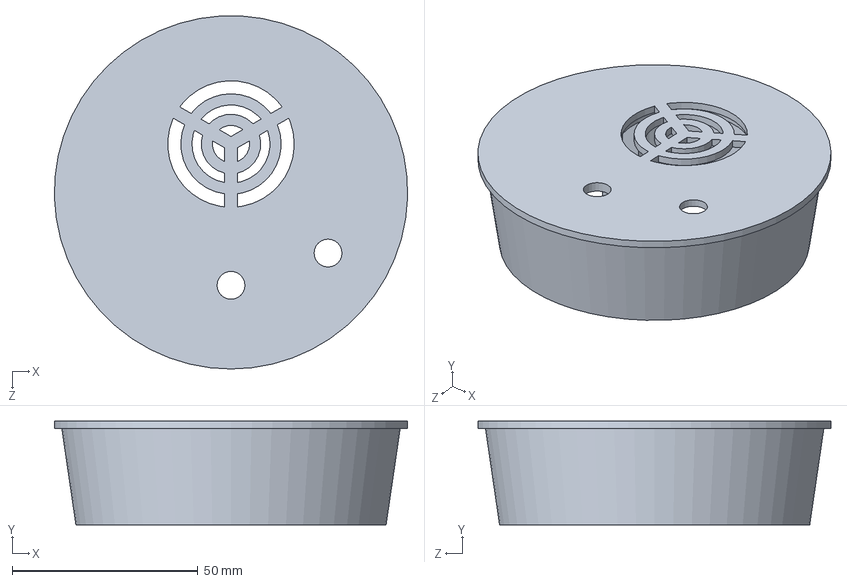
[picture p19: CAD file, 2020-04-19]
cad_design/cap-for-16oz-cup/cap-for-cup-v2.SLDPRT
95.0 x 27.9 x 94.9 mm

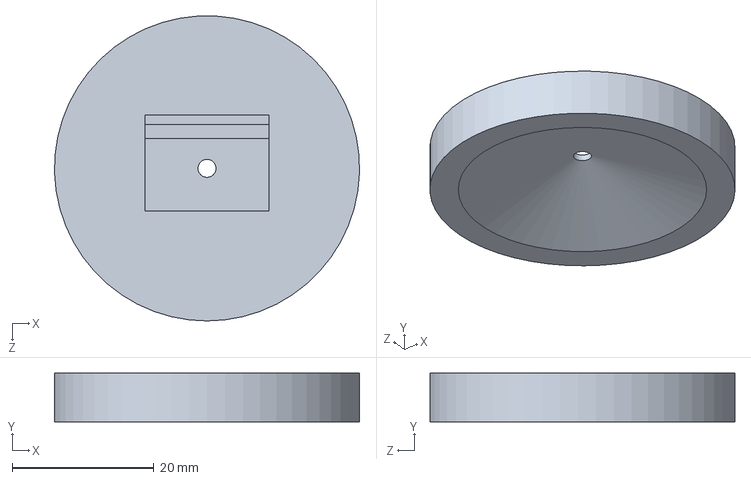
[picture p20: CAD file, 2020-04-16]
cad_design/mems-microphone-4-aaron/mems-mic-holder-bell.SLDPRT
43.0 x 6.86 x 43.0 mm

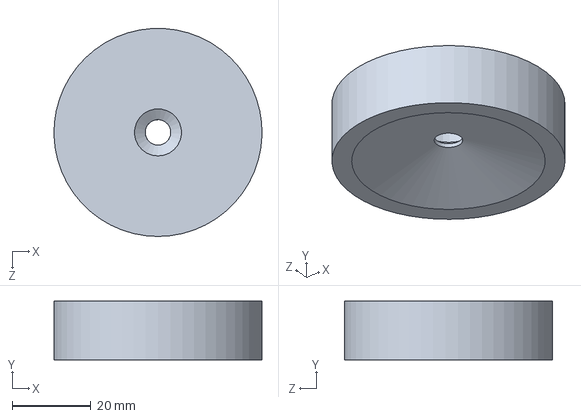
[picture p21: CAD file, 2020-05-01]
cad_design/mic-holder-bell-for-hoses/puck-and-nipple.SLDPRT
53.0 x 15.0 x 53.0 mm

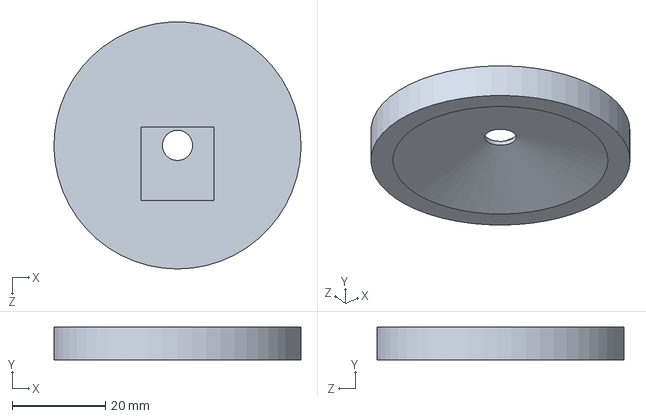
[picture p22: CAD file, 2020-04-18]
cad_design/mic-holder-bell/microphone-holder-puck-style.SLDPRT
53.0 x 7.00 x 53.0 mm

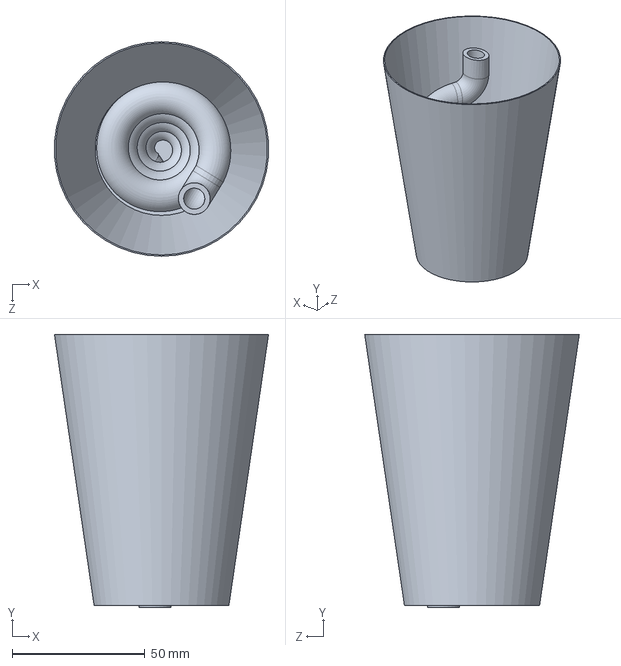
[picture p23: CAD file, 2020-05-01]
cad_design/mic-holder-long-travel-bell/LongTravelSpiralBell.SLDPRT
80.6 x 102.8 x 80.8 mm

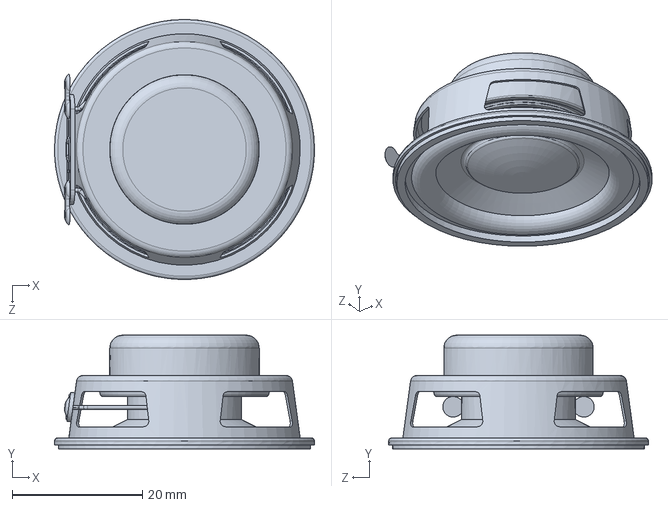
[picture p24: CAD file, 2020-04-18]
cad_design/speaker/Speaker AS04004PR-R.SLDPRT
40.0 x 17.5 x 40.0 mm

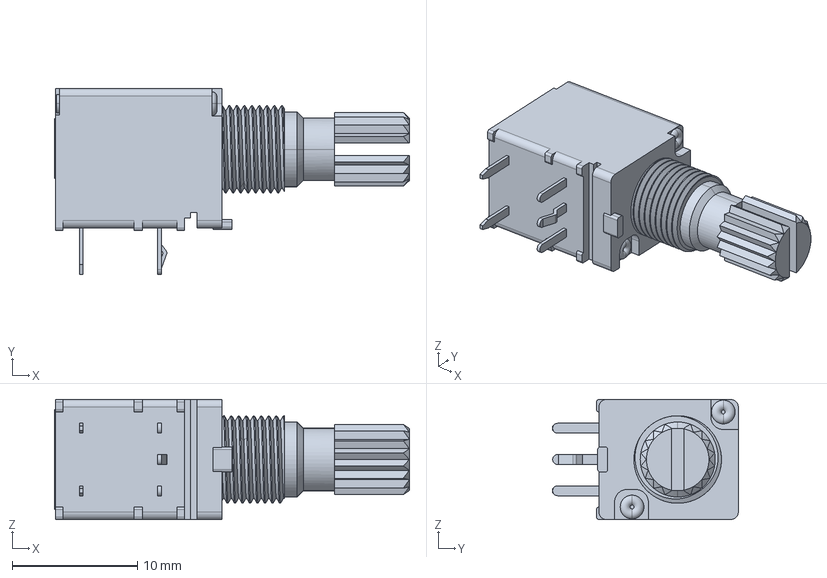
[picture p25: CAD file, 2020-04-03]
cad_design/vol-potentiometer/Volume Pot On Off ptr901-2x15k-xxxx.stp
28.4 x 14.9 x 9.60 mm

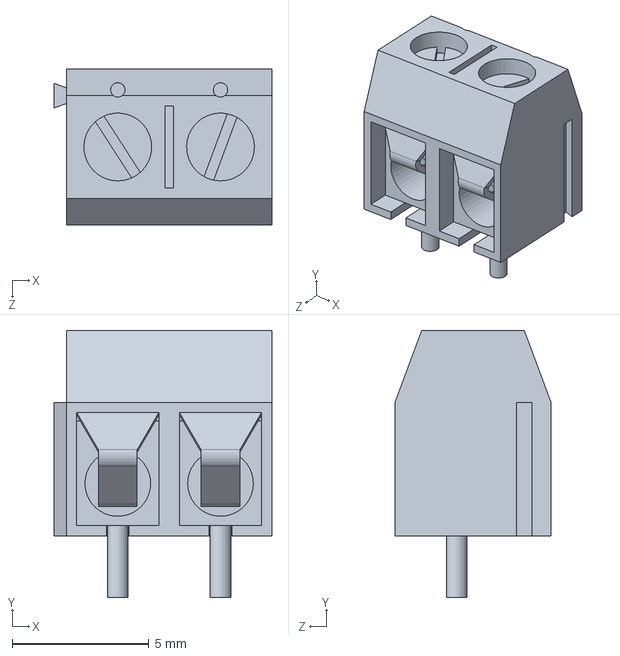
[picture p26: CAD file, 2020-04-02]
cad_design/adafruit-audio-amp/Jack.SLDPRT
7.95 x 9.75 x 5.70 mm

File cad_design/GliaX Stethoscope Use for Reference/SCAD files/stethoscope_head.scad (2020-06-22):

$fn=365;

// Take output for original head and put it in one module
module original_head() {
    union(){translate(v = [0, 0, 17.8])
    mirror(v = [0, 0, 1])
    difference(){union(){intersection(){translate(v = [-50.0, -50.0])
    cube(size = [100, 100, 17.8]);
    union(){cylinder(h = 1.080, r = 21.715);
    translate(v = [0, 0, 1.08])
    cylinder(h = 1.060, r = 21.000);
    translate(v = [0, 0, 2.14])
    cylinder(h = 0.800, r = 22.150);
    translate(v = [0, 0, 2.9400000000000004])
    cylinder(h = 3.260, r1 = 22.150, r2 = 10.500);
    translate(v = [0, 0, 6.2])
    cylinder(h = 1.300, r1 = 10.500, r2 = 8.475);
    translate(v = [0, 0, 7.5])
    cylinder(h = 13.500, r1 = 8.475, r2 = 13.500);
    translate(v = [0, 0, 21.0])
    cylinder(h = 4.000, r1 = 13.500, r2 = 16.375);
    translate(v = [0, 0, 25.0])
    cylinder(h = 0.800, r = 15.500);
    translate(v = [0, 0, 25.8])
    cylinder(h = 1.420, r = 17.215);
    translate(v = [0, 0, 13.5])
    rotate(a = [90, 0, 0])
    difference(){union(){cylinder(h = 20, r = 5.450);
    translate(v = [0, 0, 20])
    difference(){cylinder(h = 20.300, r = 4.250);
    translate(v = [0, 0, 13.8])
    union(){cylinder(h = 6.500, r1 = 2.500, r2 = 3.250);
    translate(v = [0, 0, 6.5])
    cylinder(h = 1, r = 3.250);
    }
    }
    }
    translate(v = [0, 0, -0.01])
    cylinder(h = 40.320, r = 2.650);
    }
    }
    }
    cylinder(h = 17.800, r = 21.000);
    }
    union(){translate(v = [0, 0, -0.01])
    difference(){cylinder(h = 0.570, r = 20.450);
    translate(v = [0, 0, -0.01])
    cylinder(h = 0.590, r = 17.850);
    }
    translate(v = [0, 0, 0.56])
    union(){translate(v = [0, 0, 2.735])
    mirror(v = [0, 0, 1])
    rotate_extrude(convexity = 10){polygon(points = [[0.0, 0], [0.25, 0], [0.5, 0], [0.75, 0], [1.0, 0], [1.25, 0.16], [1.5, 0.46], [1.75, 0.72], [2.0, 0.85], [2.25, 0.93], [2.5, 0.96], [2.75, 0.99], [3.0, 1.02], [3.25, 1.05], [3.5, 1.085], [3.75, 1.12], [4.0, 1.15], [4.25, 1.18], [4.5, 1.215], [4.75, 1.2475], [5.0, 1.278], [5.25, 1.308], [5.5, 1.34], [5.75, 1.372], [6.0, 1.401], [6.25, 1.432], [6.5, 1.465], [6.75, 1.5], [7.0, 1.529], [7.25, 1.559], [7.5, 1.5925], [7.75, 1.63], [8.0, 1.659], [8.25, 1.69], [8.5, 1.7225], [8.75, 1.76], [9.0, 1.7875], [9.25, 1.811], [9.5, 1.849], [9.75, 1.88], [10.0, 1.91], [10.25, 1.94], [10.5, 1.9725], [10.75, 2.005], [11.0, 2.035], [11.25, 2.065], [11.5, 2.1], [11.75, 2.134], [12.0, 2.1675], [12.25, 2.199], [12.5, 2.23], [12.75, 2.2625], [13.0, 2.291], [13.25, 2.32], [13.5, 2.3575], [13.75, 2.39], [14.0, 2.42], [14.25, 2.45], [14.5, 2.48], [14.75, 2.518], [15.0, 2.5475], [15.25, 2.5775], [15.5, 2.6125], [15.75, 2.6475], [16.0, 2.68], [16.25, 2.735], [16.7, 2.735], [0, 2.735]]);
    }
    translate(v = [0, 0, -2])
    cylinder(h = 2, r = 16.700);
    }
    translate(v = [0, 0, 13.5])
    rotate(a = [90, 0, 0])
    translate(v = [0, 0, -0.01])
    cylinder(h = 40.320, r = 2.650);
    translate(v = [0, 0, -0.01])
    cylinder(h = 27.240, r = 3.440);
    }
    }
    cylinder(h = 1.700, r = 5.000);
    }
}

//Create ring to subtract
module ring () {
    translate([0,0,12.8])
    difference() {
        cylinder(h = 6, r = 25);
        cylinder(h = 6, r = 20);
    }
}

// Create final model by subtracting ring from head
difference() {
    original_head();
    ring();
}



translate([-1,-40.2-2.5,.05])cube([2,5,.2]);
translate([0,-40.2-1,.05])difference(){
    cylinder(r=5,h=.5);
    translate([-6,0,0])cube([12,12,1]);
}

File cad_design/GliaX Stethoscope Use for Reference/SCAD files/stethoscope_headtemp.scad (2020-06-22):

$fn=365;

// Take output for original head and put it in one module
module original_head() {
    union(){translate(v = [0, 0, 17.8])
    mirror(v = [0, 0, 1])
    difference(){union(){intersection(){translate(v = [-50.0, -50.0])
    cube(size = [100, 100, 17.8]);
    union(){cylinder(h = 1.080, r = 21.715);
    translate(v = [0, 0, 1.08])
    cylinder(h = 1.060, r = 21.000);
    translate(v = [0, 0, 2.14])
    cylinder(h = 0.800, r = 22.150);
    translate(v = [0, 0, 2.9400000000000004])
    cylinder(h = 3.260, r1 = 22.150, r2 = 10.500);
    translate(v = [0, 0, 6.2])
    cylinder(h = 1.300, r1 = 10.500, r2 = 8.475);
    translate(v = [0, 0, 7.5])
    cylinder(h = 13.500, r1 = 8.475, r2 = 13.500);
    translate(v = [0, 0, 21.0])
    cylinder(h = 4.000, r1 = 13.500, r2 = 16.375);
    translate(v = [0, 0, 25.0])
    cylinder(h = 0.800, r = 15.500);
    translate(v = [0, 0, 25.8])
    cylinder(h = 1.420, r = 17.215);
    translate(v = [0, 0, 13.5])
    rotate(a = [90, 0, 0])
    difference(){union(){cylinder(h = 20, r = 5.450);
    translate(v = [0, 0, 20])
    difference(){cylinder(h = 20.300, r = 4.250);
    translate(v = [0, 0, 13.8])
    union(){cylinder(h = 6.500, r1 = 2.500, r2 = 3.250);
    translate(v = [0, 0, 6.5])
    cylinder(h = 1, r = 3.250);
    }
    }
    }
    translate(v = [0, 0, -0.01])
    cylinder(h = 40.320, r = 2.650);
    }
    }
    }
    cylinder(h = 17.800, r = 21.000);
    }
    union(){translate(v = [0, 0, -0.01])
    difference(){cylinder(h = 0.570, r = 20.450);
    translate(v = [0, 0, -0.01])
    cylinder(h = 0.590, r = 17.850);
    }
    translate(v = [0, 0, 0.56])
    union(){translate(v = [0, 0, 2.735])
    mirror(v = [0, 0, 1])
    rotate_extrude(convexity = 10){polygon(points = [[0.0, 0], [0.25, 0], [0.5, 0], [0.75, 0], [1.0, 0], [1.25, 0.16], [1.5, 0.46], [1.75, 0.72], [2.0, 0.85], [2.25, 0.93], [2.5, 0.96], [2.75, 0.99], [3.0, 1.02], [3.25, 1.05], [3.5, 1.085], [3.75, 1.12], [4.0, 1.15], [4.25, 1.18], [4.5, 1.215], [4.75, 1.2475], [5.0, 1.278], [5.25, 1.308], [5.5, 1.34], [5.75, 1.372], [6.0, 1.401], [6.25, 1.432], [6.5, 1.465], [6.75, 1.5], [7.0, 1.529], [7.25, 1.559], [7.5, 1.5925], [7.75, 1.63], [8.0, 1.659], [8.25, 1.69], [8.5, 1.7225], [8.75, 1.76], [9.0, 1.7875], [9.25, 1.811], [9.5, 1.849], [9.75, 1.88], [10.0, 1.91], [10.25, 1.94], [10.5, 1.9725], [10.75, 2.005], [11.0, 2.035], [11.25, 2.065], [11.5, 2.1], [11.75, 2.134], [12.0, 2.1675], [12.25, 2.199], [12.5, 2.23], [12.75, 2.2625], [13.0, 2.291], [13.25, 2.32], [13.5, 2.3575], [13.75, 2.39], [14.0, 2.42], [14.25, 2.45], [14.5, 2.48], [14.75, 2.518], [15.0, 2.5475], [15.25, 2.5775], [15.5, 2.6125], [15.75, 2.6475], [16.0, 2.68], [16.25, 2.735], [16.7, 2.735], [0, 2.735]]);
    }
    translate(v = [0, 0, -2])
    cylinder(h = 2, r = 16.700);
    }
    translate(v = [0, 0, 13.5])
    rotate(a = [90, 0, 0])
    translate(v = [0, 0, -0.01])
    cylinder(h = 40.320, r = 2.650);
    translate(v = [0, 0, -0.01])
    cylinder(h = 27.240, r = 3.440);
    }
    }
    cylinder(h = 1.700, r = 5.000);
    }
}

//Create ring to subtract
module ring () {
    translate([0,0,12.8])
    difference() {
        cylinder(h = 6, r = 25);
        cylinder(h = 6, r = 20);
    }
}

// Create final model by subtracting ring from head
difference() {
    original_head();
   // ring();
}



translate([-1,-40.2-2.5,.05])cube([2,5,.2]);
translate([0,-40.2-1,.05])difference(){
    cylinder(r=5,h=.5);
    translate([-6,0,0])cube([12,12,1]);
}

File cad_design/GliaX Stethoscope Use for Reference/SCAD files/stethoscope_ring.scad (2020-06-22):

$outside_width = 41.5/2; //Radius of outside wall (mm)
$inside_width_diaphragm = 18; // Inside radius of diaphragm (mm)
$inside_width_wall = 20; //Inside radius of wall (mm)

// Bottom ring
module bottom_ring($fn=360) {
    difference() {
        cylinder(h = 0.5, r = $outside_width);
        cylinder(h = 0.5, r = $inside_width_diaphragm);
    }
}

// Side wall
module side_wall($fn=360) {
    difference() {
        cylinder(h = 6, r = $outside_width);
        cylinder(h = 6, r = $inside_width_wall);
    }
}

//Compile both rings
union() {
    bottom_ring();
    side_wall();
}

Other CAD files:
cad_design/GliaX Stethoscope Use for Reference/angle test.SLDPRT
cad_design/cap-for-16oz-cup/speaker-retainer-ring.SLDPRT
cad_design/GliaX Stethoscope Use for Reference/Head Diaphragm Template(Cutting Guide).stl
cad_design/mems-microphone-4-aaron/i2s_mems_mic_board.SLDPRT
cad_design/16-oz-plastic-cup/16-oz-plastic-cup.SLDDRW
cad_design/GliaX Stethoscope Use for Reference/ring.stl
cad_design/GliaX Stethoscope Use for Reference/ring_.SLDPRT
cad_design/adafruit-audio-amp/.100 Header.SLDPRT
cad_design/adafruit-audio-amp/ARDUINO AUDIO AMP MAX98306 987.IGS
cad_design/adafruit-audio-amp/ARDUINO AUDIO AMP MAX98306 987.SLDASM
cad_design/adafruit-audio-amp/ARDUINO AUDIO AMP MAX98306 987.STEP
cad_design/adafruit-audio-amp/ARDUINO AUDIO AMP MAX98306.SLDPRT
cad_design/cap-for-16oz-cup/cap-for-cup-fit-test.SLDPRT
cad_design/cap-for-16oz-cup/cap-for-cup-v2.STL
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

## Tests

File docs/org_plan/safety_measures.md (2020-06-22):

## Safety measures

Currently all work on the Covid-19 Bluetooth Stethoscope project is remote, with volunteers spread around the world working from their homes.  There are no physical spaces or assets associated with the project at this time.  If this changes, we can utilize the ICS 208 Site Safety and Control Plan.

If we acquire and distribute materials to makerspaces or volunteers we will take measures to minimize contact and package materials safely.

## Stethoscope designs

For stethoscope designs themselves, our primary safety concern is sanitation.  Our ideal solution is to have a durable, smooth-sided housing that is sealed and can be easily sanitized with current practices - commonly used disinfectants O3 and/or UV light.  If that isn't possible due to necessary openings like a speaker grill or rough 3D-printed material, then devices can be placed in a ziploc bag that can be sanitized or discarded between uses provided audio quality is sufficient. 

There is no case where a faulty device could harm the patient or provide a false reading for the medical professional.  Medical professionals are trained in stethoscope use and if a device fails or they cannot hear appropriate audio the fallback solution would be to use a standard stethoscope, so the worst-case option is equivalent to the current standard solution.

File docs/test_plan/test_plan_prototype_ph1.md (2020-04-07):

#  Quick and Dirty Speaker
*(Note, Quick and Dirty Speaker design only uses analog components)*

## Prototype Test Plan

### Equipment

Received first shipment of Digikey component parts.  7Apr2020
 - Access to Shop Power supply, Model: GPC-3020
 - Analog oscilloscope
 - Basic Electronic Hand Tools
 - Decent volt-ohmmeter
 - 3D Printer (PLA & ABS material)

### Target Goals
Understand if initial design decisions are sound
 - Was 3 watts the right power target for amplified audio system?
 - Is feedback between Microphone and Speaker an issue for us?
 - Understand the relationship between battery power and amplification.  What system voltage should we be using (3.0v or 4.5v or something else).
 - Quantify current draw in different use conditions, predict expected battery life for our use case.
 - Does a variation in microphone supply power affect audio output?

Understand which microphone makes the most sense for us
 - Analog MEMS vs Electret Condenser Element?
 - UniDirectional vs OmniDirectional?
 - Noise filtering vs not?
 - CUI Mic Dev Kit, MIC5=MEMS Omni, MIC6=Electret Noise Cancelling, MIC7=Electret Uni , MIC8=Electret Omni

### Question for EE folks... can we look at microphone circuit output on an oscilloscope with a focus on amplitude peak height and use that as a quantifiable indicator of microphone performance ?? ###

 Take an initial stab at the input bell 3d Design
 - Shallow cone (like the GliaX Design)
 - Deeper cone

 Figure out the resistance value for the volume adjust potentiometer.
 Spec sheet for the AdaFruit amplifier suggested 50KΩ, but we were unable to find any of those parts available with convenient integral on-off switch.  Although that design exists, suppliers are all out of stock. 10KΩ and 100KΩ Logarithmetic on-off & potentiometer components are available.

 - 10KΩ Logarithmetic
 - 50KΩ Logarithmetic
 - 100kΩ Logarithmetic

 Was Logarithmetic potentiometer the correct choice for our analog design?  *If necessary* borrow linear components from friend and test:
 - Logarithmetic
 - Linear  

 Speaker Manufacturer?  We picked two different 3 watt speakers.  Does that make a difference?
 - 	PUI Audio, Inc.	Mfgr PN: AS04004PR-R
 - 	DB Unlimited  Mfgr PN: SP520104-1

## Lets Start Testing
 - Figure out who's going where and when.  
 - Add soldered on pins or sockets to each component accordingly. Plug and Play !!

 ### Dual Power Supply testing
 Setup dual power supply.  Power microphone separately from audio amp. Simple benchtop testing.  The intent is to optimize power choices, then test, lock that in, go to one power supply and measure current draws in next phase.  

#### #Prototype_phase_one_#1
 - PUI speaker
 - 50K pot
 - Adafruit audio amp (4.5v input power)
 - MIC5, no hockey puck cone  (target 2.0v supply power, min=1.6v, max=3.6v)
 - vary speaker volume via pot?  Results?
 - Vary audio input voltage from 3v to 6v.  What happens?  Take notes...
 - Vary mic power, results?

#### #Prototype_phase_one_#2
 - PUI speaker
 - 50K pot
 - Adafruit audio amp (4.5v input power)
 - MIC6, no hockey puck cone  (target audio amp Vdd as mic supply power, min=2.0v, max=10v)
 - vary speaker
 - Vary audio input voltage from 3v to 6v.  What happens?  Take notes...
 - Vary mic power, results?

#### #Prototype_phase_one_#3
 - PUI speaker
 - Adafruit audio amp (4.5v input power)
 - MIC7, no hockey puck cone  (target audio amp Vdd as mic supply power, min=2.0v, max=10v)
 - Vary audio input voltage from 3v to 6v.  What happens?  Take notes...
 - Vary mic power, results?

#### #Prototype_phase_one_#4
 - PUI speaker
 - Adafruit audio amp (4.5v input power)
 - MIC8, no hockey puck cone  (target audio amp Vdd as mic supply power, min=2.0v, max=10v)
 - Vary audio input voltage from 3v to 6v.  What happens?  Take notes...
 - Vary mic power, results?

#### #Prototype_phase_one_#5
 - Pick one of the above systems.  
 - Play with different potentiometers (10KΩ, 50KΩ, 100KΩ), Results?
 - Vary audio amp voltage, test potentiometers again. Results?

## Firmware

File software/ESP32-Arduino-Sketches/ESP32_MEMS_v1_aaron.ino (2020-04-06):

/* UDP audio streamer with ESP32 and MEMS I2S mic
 * Resources:
 * https://www.hackster.io/julianso/esp32-voice-streamer-52bd7e
 * https://superuser.com/questions/597227/linux-arecord-capture-sound-card-output-rather-than-microphone-input
 * https://esp32.com/viewtopic.php?f=19&t=4997
 * to play live:
 *         nc -l -u 7777 | aplay -r 44100 -f S32_LE -c2
 * convert to wav file:  
 *         nc -l -u 7777 > test32.dump
 *         sox -t raw -r 44100 -e unsigned-integer -L -b 32 -c 2 test32.dump output.wav
*/
#include <Arduino.h>
#include <WiFi.h>
#include <driver/i2s.h>

// setup I2S
const i2s_port_t I2S_PORT = I2S_NUM_0;

// Wireless network setup
const char* ssid     = "[YOUR WIFI SSID]";
const char* password = "[PASSWORD]";

// remote port
const int port   = 7777;
const char* host = "192.168.86.242";

// UDP client
WiFiUDP client;

// init
void setup() {    
  // for debugging  
  Serial.begin(500000);

  // seutp wireless, don't bother with event handling
  WiFi.mode(WIFI_STA);
  WiFi.begin(ssid, password);
  while (WiFi.status() != WL_CONNECTED) {
    delay(500);
    Serial.print(".");
  }
  Serial.println("");
  Serial.println("WiFi connected.");
  Serial.println("Leased IP address: ");
  Serial.println(WiFi.localIP());

  // The I2S config as per the example
  const i2s_config_t i2s_config = {
      .mode = i2s_mode_t(I2S_MODE_MASTER | I2S_MODE_RX), 
      .sample_rate = 44100,                         
      .bits_per_sample = I2S_BITS_PER_SAMPLE_32BIT, 
      .channel_format = I2S_CHANNEL_FMT_RIGHT_LEFT, 
      .communication_format = I2S_COMM_FORMAT_I2S_MSB,
      .intr_alloc_flags = ESP_INTR_FLAG_LEVEL1,      
      .dma_buf_count = 4, 
      .dma_buf_len = 8    
  };

  // pin config as per the setup
  const i2s_pin_config_t pin_config = {
      .bck_io_num = 14,   // BCKL
      .ws_io_num = 15,    // LRCL
      .data_out_num = -1, // not used (only for TX)
      .data_in_num = 32   // DOUT
  };

  // setup pins
  pinMode(32, INPUT);
  pinMode(14, OUTPUT);
  pinMode(15, OUTPUT);

  // Configuring the I2S driver and pins.
  // This function must be called before any I2S driver read/write operations.
  if (i2s_driver_install(I2S_PORT, &i2s_config, 0, NULL) != ESP_OK) {
    Serial.println("Failed installing driver!");
    while (true);
  }
  if (i2s_set_pin(I2S_PORT, &pin_config) != ESP_OK) {
    Serial.println("Failed configuring pins.");
    while (true);
  }
  Serial.println("I2S driver installed.");

  // setup UDP client  
  client.beginPacket(host,port);
}

// main logic
void loop() {
  uint32_t sample;

  // read samples without timeout
  int bytes_read = i2s_pop_sample(I2S_PORT, (char *)&sample, portMAX_DELAY); 

  // convert to byte and dump to UDP 
  byte *p;
  p = (byte*)&sample;
  client.write(p,sizeof(p));
}

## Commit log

2020-03-27 Add inital review materials
2020-03-28 Attach to stethoscope concept
2020-03-29 Added reflective-pulse-oximetry circuit image.
2020-03-31 minor updates to file with esp32 stuff
2020-04-01 Minor updates to txt file, re: amp board
2020-04-01 start adding CAD reference files
    [heltec_wifi_32_asm2.SLDPRT]
2020-04-01 Added CAD solid models of AA battery, speaker
    [AS04004PR-R.igs, Speaker AS04004PR-R.SLDPRT]
2020-04-01 renamed folder name to esp32
    [heltec_wifi_32_asm2.SLDPRT]
2020-04-01 update AA battery Cad model
    [aa_battery.SLDPRT]
2020-04-02 Add adafruit audio amp info for CAD design
    [.100 Header.SLDPRT, ARDUINO AUDIO AMP MAX98306 987.IGS, ARDUINO AUDIO AMP MAX98306 987.SLDASM, ARDUINO AUDIO AMP MAX98306 987.STEP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]
2020-04-02 Added more CAD models
    [CUI_DEVICES_CMC-4013-SMT-TR.sldprt, CUI_DEVICES_CMC-6015-47P.sldprt, CUI_DEVICES_CMM-3312AT-44308-TR.sldprt, CUI_DEVICES_CMR-2747PB-A.sldprt]
2020-04-03 Add potentiometer volume control components
    [Volume Pot On Off ptr901-2x15k-xxxx.stp]
2020-04-03 More CAD references for Vol Adj Potentiometer
    [Volume Pot On Off ptr901-2x15k-xxxx.SLDPRT]
2020-04-04 Add files via upload
    example of siimple doppler systems; these are often used to listen to fetal heart sounds or blood flow. They cannot be sterilized but surface cleanable. When needed in sterile settings like the opera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
    Stethoscopes are never really sterile, so surface cleaning and/or use of a clean cover/sleeve is a reasonable approach when "contact precautions" are required for patient care.
2020-04-04 Add files via upload
    60 dram bottle has an inner diameter ~48 mm -- should accept speaker per current design specs
2020-04-04 onshape stuff
    [CUI_DEVICES_CMC-4013-SMT-TR.sldprt, Mic4013onBoard.SLDASM, Mic4013onBoard.x_t, Speaker AS04004PR-R.x_t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]
2020-04-05 Update CAD contents and OnShape info...
    [ARDUINO AUDIO AMP MAX98306 987 with pin mods.SLDASM, Mic4013onBoard.SLDASM, Mic4013onBoard.x_b, Mic4013onBoard.x_t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]
2020-04-05 Add STL of microphone bell to CAD directory
    [ARDUINO AUDIO AMP MAX98306 987 with pin mods.SLDASM, microphone-holder-bell.STL]
2020-04-05 Add voltage divider schematic with 4.5v power
2020-04-06 Add bell shaped holder for MEMS mic for Aaron
    [Speaker AS04004PR-R.SLDPRT, i2s_mems_mic_board.SLDPRT, mems-mic-holder-bell.SLDPRT, mems-mic-holder-bell.STL]
2020-04-06 Upgrade Mems mic bell for Aaron, reduce height to save plastic, add GilaX Stethoscope notes
    [mems-mic-holder-bell.SLDPRT, mems-mic-holder-bell.STL, microphone-holder-bell.SLDPRT]
2020-04-06 Add GliaX cross section, Aaron initial audio arduino sketch
2020-04-07 Add Quick&DirtySpeaker Prelim Prototype Test Plan
2020-04-07 Continue to update prototype test plan
2020-04-08 smarter speaker puck
    It consists of INMP441 MEMS microphone,it is interfaced to esp32 through I2S. The digital output from mic is given to DAC ,whose ouput is then connected to amplifier (pin 25).
2020-04-16 Update LBC notes, add 16 oz plastic cup
    [16-oz-plastic-cup.SLDDRW, 16-oz-plastic-cup.SLDPRT, 16-oz-plastic-cup.x_t, mems-mic-holder-bell.SLDPRT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]
2020-04-18 Lots of work on upgrading CAD files
    [16-oz-plastic-cup.SLDDRW, 16-oz-plastic-cup.SLDPRT, Speaker AS04004PR-R.SLDPRT, cap-for-cup-fit-test.SLDPRT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]
2020-04-18 Add speaker notes for cap design
    [cap-for-cup-fit-test.STL, cap-for-cup.SLDPRT, cap-for-cup.x_t]
2020-04-19 finalize details on Cup Cap and Speaker retention ring
    [QuickAndDirtyAssy.SLDASM, cap-for-cup-v2.SLDPRT, cap-for-cup-v2.STL, cap-for-cup.SLDPRT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]
2020-04-21 Update notes on Stethoscope, filters, gain, opamps
2020-04-21 Add notes on Sallen-Key Low Pass filter design
2020-04-22 Add more schematics notes for active filter design
2020-04-29 Added prototype image
2020-05-01 Added lots of white papers, notes on GliaX design, notes on active filter
    [Head Diaphragm Template(Cutting Guide).stl, LongTravelSpiralBell.SLDPRT, hose-adapter.SLDPRT, hose-adapter.STL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]
2020-06-22 Consolidate recent updates
    [Glia cone.xlsx, angle test.SLDPRT, ring.SLDPRT, ring_.SLDPRT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]
